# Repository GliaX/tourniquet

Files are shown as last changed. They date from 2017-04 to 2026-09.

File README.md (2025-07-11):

# EXERCISE CAUTION WITH CLINICAL USE Tourniquet


The design of this tourniquet is constantly being improved based on feedback from the field. While we are working very hard to prepare this tourniquet for clinical use, we do not consider it finished. Please do not deploy this unless you are in a crisis situation and know exactly what you are doing. 3D printed tourniquet is to stop bleeding, especially related to penetrating injuries.

Please read our [Design Intent document](https://github.com/GliaX/tourniquet/blob/master/quality_control/design_intent.md) before creating a pull request with any re-designs!

This tourniquet is in use [in Gaza](https://trklou.medium.com/3d-printed-open-source-tourniquet-rationale-failure-analysis-and-proposed-next-steps-of-the-glia-97e8441b4c5a) and is being produced for [emergency use in Ukraine](https://trklou.medium.com/glias-gaza-tourniquet-is-ready-for-emergency-use-in-ukraine-make-some-if-you-can-ef5f83260b7c).

## Contact
Contact person: Tarek Loubani <tarek@tarek.org> or Glia <info@glia.org>
Repository manager: Tarek Loubani

## Print settings
Print the 3MF file, modified to your needs. It's not recommended to edit the meshes - do not facet the windlass, do not squish / scale it for easier printing.

Supports are to be created based on your own printer and support settings. Please reach out if you have any questions.

Approximately 46g of material is needed to print a single copy of the 4 necessary parts.

Material: ABS
* Layer Height: 0.2 mm
* Infill: 100%
* Bed temperature: 100°C temp at the first layer to avoid warping.

Material: PETG
* Layer Height: Same as ABS
* Infill: Same as ABS
* Bed temperature: 85°C temp at the first layer to avoid warping.

### Settings Per Part:
* backing_support:
  * supports
  * 4 perimeter shells/walls
  * 2 bottom/top shells/walls
* buckle:
  * supports
  * 2 perimeter shells/walls
  * 2 bottom/top shells/walls
* clip:
  * supports
  * 4 permiter shells/walls
  * 4 bottom/top shells/walls
* windlass:
  * supports
  * 4 permiter shells/walls
  * 4 bottom/top shells/walls

## Assembly Instructions
See the assembly instruction manuals in the following languages:
* [Arabic](assembly_instructions/INSTRUCTIONS_AR.md)
* [English](assembly_instructions/INSTRUCTIONS_EN.md)
* [Ukrainian](assembly_instructions/INSTRUCTIONS_UA.md)
* [Polish](assembly_instructions/INSTRUCTIONS_PL.md)
* [French](assembly_instructions/INSTRUCTIONS_FR.md)
* [Russian](assembly_instructions/INSTRUCTIONS_RU.md)

## Tourniquet QA (Quality Assurance) Folder
In this QA folder, you will find a printable QA chart and checklist. There is also information on design intent, and tensile strength notes. 
https://github.com/GliaX/tourniquet/tree/master/quality_control

## Tourniquet staging and folding Instructions
There are several reasonable techniques for staging a CAT-style tourniquet. At Glia, we use and recommend the following technique, which is in use in Gaza: https://www.youtube.com/watch?v=CSECJQPJmLw

## Packaging Instructions
The tourniquet should be packaged in clear, thin plastic such as PVC wrap to prevent any degradation from humidity or other environmental factors. This wrap should be easy to remove with bare hands and no tools.

## Injection molding - WARNING
We have presented injection molding files in the [`injection_molding`](injection_molding) folder. The injection molded tourniquet has not yet been deployed and is in the process of being tested at this time. Follow best practices for injection molding and assemble parts as above.
The "desktop_injection" folder is highly experimental and not deployed yet. We give no guarantees to the mold's correct behavior. 

## License
See the [LICENSE file](LICENSE) for more details of the GPLv3 license. These files are also available as [Creative Commons By Attribution ShareAlike](https://creativecommons.org/licenses/by-sa/4.0/) if desired.

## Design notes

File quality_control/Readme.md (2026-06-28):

# Tourniquet Quality Control

Our [Design Intent](design_intent.md) document covers the reason for the specific design of our tourniquet parts. Please read this document before printing the parts.

There are several tools available for Quality Assurance of the manufactured tourniquet.

**Material Specs**

Here are the [Material Specs](Tourniquet_NonPrint_Material_Specs.pdf) for non-printed materials needed. These materials were sourced in Canada, so there will be differences based on your location, but please adhere to the quality of these materials as much as possible, especially with the inner strap. 

**Backplate Tester**

The [Backplate Tester](TQ_backplate_tester.STL) has been developed in order to test the backplates as they come off of the 3D printer bed. This is because of breakage that can be common when printing this part. Please see the [Backplate Breakage Report](Backplate_Breakage_Report.pdf), which talks about this issue, and also shows how to use the backplate tester.

**Strength Test for Parts**

Strength test for Buckle [video](buckle_strength_test.mp4) - insert a strap into both slots and pull apart with hands using maximum strength

Strength test for Backplate [video](backplate_strength_test.mp4)- use backplate tester above to bend backplate around the Diameter

Strength test for Clip [video](clip_strength_test.mp4)- hold both side of the clip and bend them away from each other

Strength test for Rod [video](rod_strength_test.mp4)- push with hands at maximum strength with thumbs on slot and also adjacent to slot

**Strap Spacer**

The [Strap Spacer](strap_spacer.stl) is a tool that can be used in order to ensure the inner strap has the correct slack needed when assembling and sewing the tourniquet together.

The material and printing settings do not matter as long as the dimensions of the spacer are accurate.
This part is a tool, not an integral element of the tourniquet and does not need to meet the rigidity requirements of the windlass, backplate, buckle or clip.

Please see step #10 in the assembly instructions on how to use the strap spacer when manufacturing the tourniquet.

**QA Chart and Checklist**

The Tourniquet [QA Chart](tourniquet_QA_Chart.pdf) and [QC Checklist](tourniquet_QC_checklist_x2.pdf) are tools to be used when conducting a quality assurance check on the finished manufactured tourniquet. These tools ensure that all the details are given attention to check if they adhere to the manufacturing specifications in the assembly instructions, and that the device will function properly when used.

**Measuring Tool**

The [Tourniquet Measuring Tool](tourniquet_measuring_tool.pdf) can be used when conducting the quality assurance of each manufactured device. This is a simple device printed on paper that can help with the QA process in terms of quickly checking that 3 important measurements are correct:

1. the distance from the rounded end of strap to the closest edge of the box stitch (30mm)

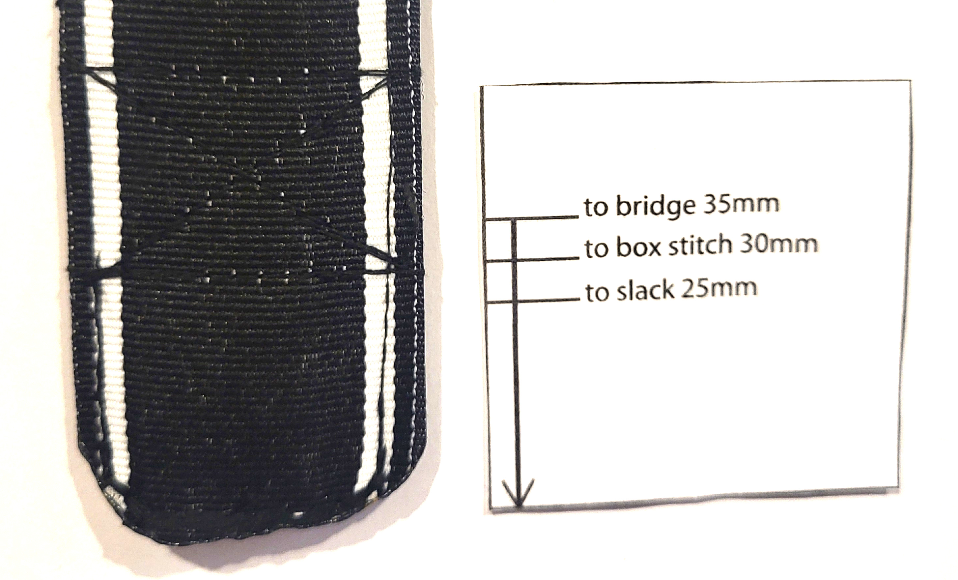
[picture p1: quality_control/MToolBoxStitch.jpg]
Box Stitch

:-

2. the amount of slack on the inner strap (25mm)

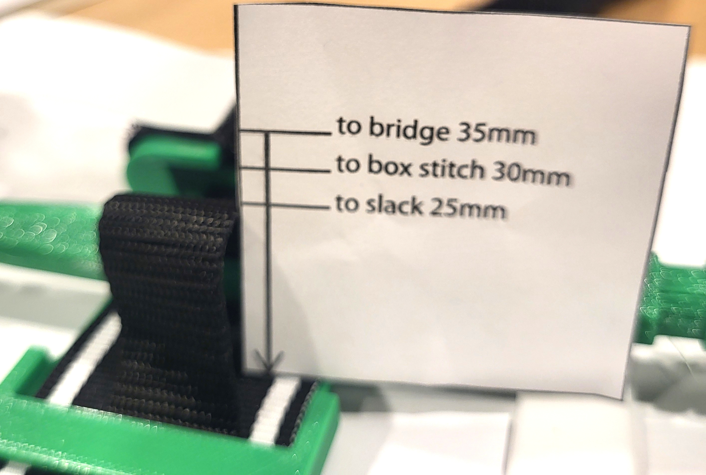
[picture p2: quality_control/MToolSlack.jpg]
Slack

:-

3. the distance from the bridge of the backplate to the stitch holding the buckle to the strap (35mm)

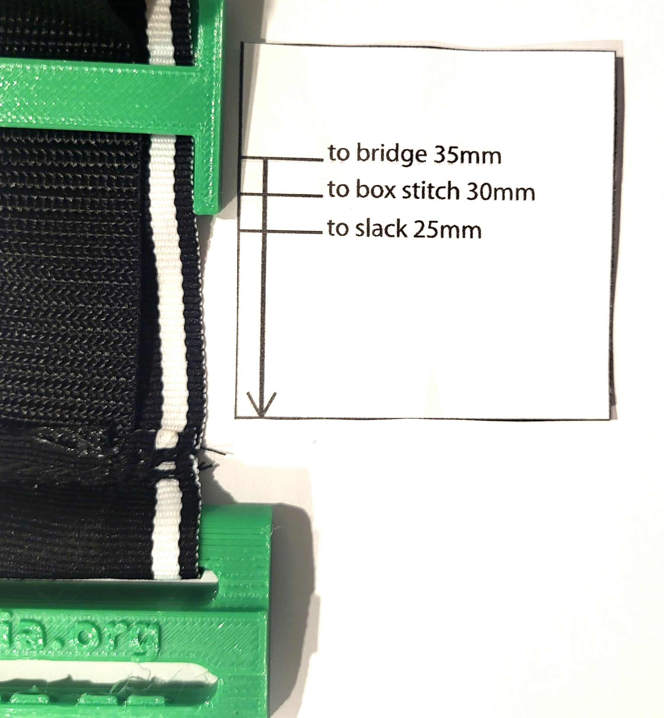
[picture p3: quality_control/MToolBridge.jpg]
Bridge

:-

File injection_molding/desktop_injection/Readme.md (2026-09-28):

# Desktop injection molding 
This folder details the Glia Poland's experimental desktop injection molding process for the plastic parts of the Glia Tourniquet. It details our journey and any pitfalls we have encountered over the months of working at the project, any tips and tricks and the methodology we have established along the way. Please read through it carefully in its entirety before attempting to injection mold your own tourniquet parts. 

# Files
This folder contains files for prototypical molds for all four parts of the Tourniquet to be printed on a resin 3D printer. Each of the molds height is 10cm and they have a universal slot for the aluminium insert that matches our machine's nozzle. The resin compound that is used for printing is brittle and would not withstand the pressure nor the high temperature of the injection molder nozzle so the part of the mold that directly touches it needs to be made of metal, aluminium being the easiest one to machine out. We have provided a file for the insert under the name of "nozzle_slot.FCStd". The nozzle block is split in the middle - when milling you need to put two 2cmx3cmx1cm thick blocks in the vice. 
We also include an edited file for a reinforced windlass and clip used in the molds.  

### Aluminium molds
The folder "aluminium_milled" contains edited molds for milling them out of metal on a 3-axis CNC machine. They will require modification to change over the nozzle shape to the machine that you are using. You should aim to create aluminium molds - the resin is great for prototyping and setting up the machine/testing out plastics, but shatters easily and does not permit long runs. An average aluminium mold longevity is between 2000 - 10000 parts, compared to around 10 using the Siraya Tech Ultra White resin. Stronger engineering resins exist which could provide a longer run, but we have not tested them out.

# Our machine
We are using the [Buster Beagle mk3 injection molding machine](https://www.busterbeagle3d.com/) with the SC100 piston. The mk3 has been confirmed to have enough plastic volume to inject the biggest part of the tourniquet - the windlass. Its main drawback is the weak workholding - a 2 ton vice - which we supplement with [C-clamps](https://www.amazon.com/Edward-Tools-Heavy-Steel-Clamp/dp/B086FRTJF4/). Later on we plan to implement an automated pneumatic vice system that will give us more reliable setting times and ease the handling of the process. 

# Our plastic
Initially we injected the parts with ABS pellet. This proved to be difficult to perform with a DIY injection molder and gave us inconsistent results. The amount of [splay](https://en.wikipedia.org/wiki/Splay_(plastics)) and [delamination](https://en.wikipedia.org/wiki/Delamination) made the parts unacceptable and in effect we decided to switch the plastic to [HDPE](https://en.wikipedia.org/wiki/High-density_polyethylene) which has a better melting and flowing abilities.
We suggest using already coloured, virgin pellets which can be obtained from online retailers or local plastic markets. The pellet needs to be injection molding grade and have an MFI (Melt Flow Index) of minimum 8. Natural white pellets may show discoloration in the part if injected at higher temperatures but is generally easier to inject as color additives often make the HDPE absorb moisture from air and moist plastic needs to be dried before injecting. Powdered pigment can be used in the Buster Beagle machine, although it leads to uneven coloration due to the lack of a mixing screw that is present in larger injection molders.

### What about reground?
Recycled plastic can be used, provided it did not absorb moisture and that the injected part does not perform worse than virgin pellets. Another issue is the fact that recycling companies sometimes mix different plastic subtypes together making it very hard to determine the end result and rigidity of the final part. 

# Anything else I need?
### A compressor
You need a car compressor to power the Buster Beagle piston. We previously used [a small 8 bar 20l compressor](https://sklep.kupczyk.pl/kompresor-tlokowy-fl-24-kupczyk,3,19543,2316), but changed to a larger one after a few months. Currently we are using a [10 bar 115l compressor](https://narzedziapremium.pl/produkt/sprezarka-kompresor-olejowy-115l-v-2065-bjc/) as it's work cycles are longer. It has a regulator at the end, and a quick-release, in case we need to use the compressed air to power something else. A bigger compressor is also needed for the further plans of automating the process. Remember to always wear ear protection when working near a compressor device!

### A small oven
There are [cheap, small ovens](https://www.amazon.com/BLACK-DECKER-TO1313SBD-4-Slice-Toaster/dp/B00GGFHH4U/?th=1) that will be used for drying the pellets and for warming up the molds. They cannot substitute a professional dryer, but cost a fraction of the money and help quite a bit. You should be drying everything hygroscopic that goes into the machine, regardless of the pellets used - whether they are recycled or new. Drying helps immensly with humid environments. Make sure the oven you're buying has a "warm" setting - that it goes under 100 degrees C. 
**Do not use your home oven to dry plastic**

### Alternative to small oven: tumbling dryer
**You probably want a seperate dryer for clothes and for plastic - especially if using colored. This will probably dirty up your clothes with plastic and is possibly a health risk.**
A tumbling clothes dryer works better than an oven on ABS, resulting in strong parts that only have cosmetic defects. You need a cloth sack, fill it with plastic, tie it off with a ziptie and throw it into a dryer. Make sure the heat is set to low - you probably want to be drying the pellets at around 80 degrees C. 

### Alternative to small oven or tumbling dryer: industrial drying machine
To completely solve the moisture problem, you need to have an industrial grade drying machine. They are rather expensive to get, as of 11.05.2023 costing around 2000 euro netto, with other companies reaching 3000 or 4000. There are two technologies that work - either an air powered dryer from a compressor, or one equipped with molecular sieves. You would want a dew point of around -20 degrees Celsius. 

### Safety Eguipment
Always wear a full face mask with a chemical filter while doing injection molding.
Wear overall safety suit and protective shoes and gloves in your workshop, keep them clean and aside from your regular clothes. This is due to the possibility of the fumes and microplastics contaminating your attire.
Always wear ear protecting mufflers when working near an air compressor running. 

**Full Bill of Materials and safety equipment list along with purchase links are available as .ods and .csv files under the name glia_poland_bill_of_materials in the path tourniquet/injection_molding/desktop_injection**

# How do I make a mold?
We are printing our prototype molds in Siraya Tech Ultra White on the Anycubic Photon Mono X 6k. This tutorial assumes you know the basics of resin printing.
We also mill out our molds out of aluminium, which results in molds that we use in production. 
### Safety 
Resin printing is a messy and toxic process, the first steps are to make sure you are safe. Wear nitrile gloves, safety glasses and a respirator or mask. Do not get any of the resin on your skin. Process any trash from the printing by hardening everything using a UV flashlight (wear UV safety glasses when doing this). Do not touch, sniff, throw away uncured parts or supports. Clean any spill with isopropyl alcohol. Have an air purifier with a HEPA filter in your workshop or work in a well ventilated area. [Read safety best practices for resin printing](https://all3dp.com/2/sla-3d-printing-is-3d-printer-resin-toxic/)
### Settings
We are printing with the following settings: 
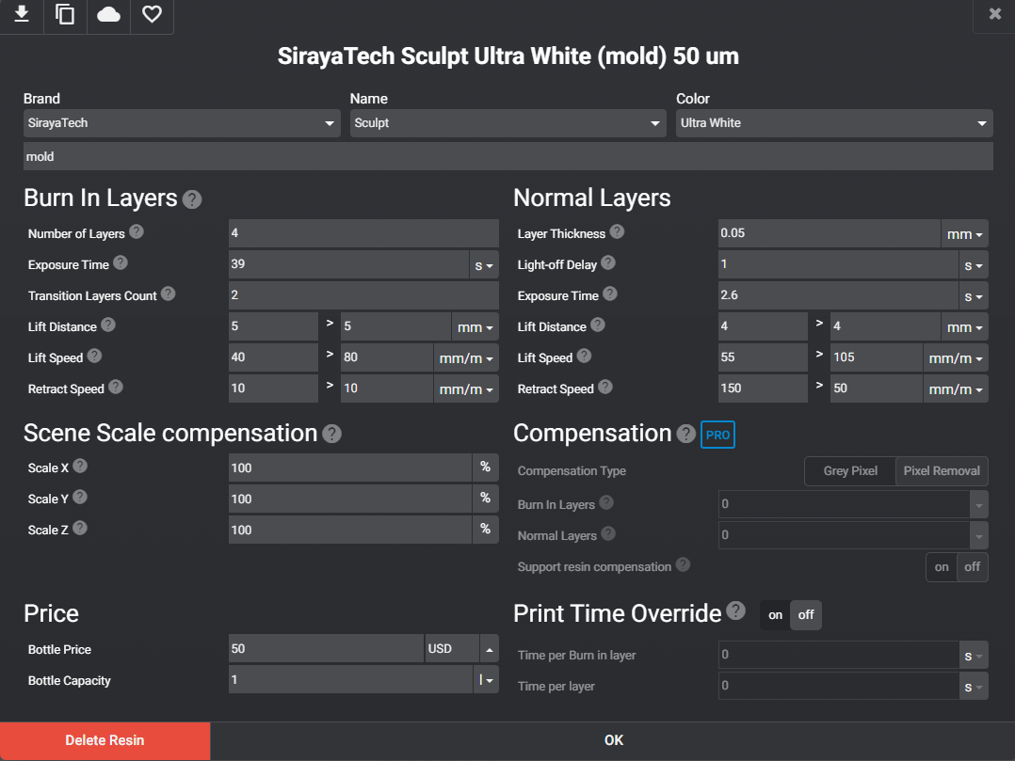
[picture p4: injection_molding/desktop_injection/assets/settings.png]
Illustration 1


### Print orientation
We are printing the molds standing up, off the baseplate, on supports. We have tried other orientations that provide a shorter print, but we encountered issues with the peel forces being too great and ruining it. We angle the print away by 2 - 3 degrees, so the supports don not touch the surface, requiring sanding.  

### Presupporting the file
We use two slicers to prepare files for print. We use PrusaSlicer for its autosupport feature and better supports, then we export the plate with supports and slice the file using Lychee. We need to add more supports on the bottom in PrusaSlicer, see a sample density in the pic below. Otherwise the print falls of the plate under the peel forces/its own weight. We tend to oversupport the print to avoid wasting resin in a failure. 
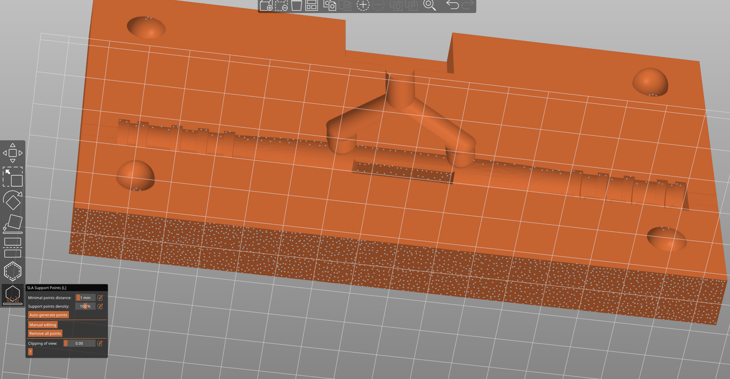
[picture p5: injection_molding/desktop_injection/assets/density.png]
Illustration 2


### Tolerances
Some files might require sanding and fitting. You should be able to open the empty molds without any issue / them getting stuck. 

# Which one do I start with?
The easiest part to inject is the buckle. It has a very small and simple mold that does not require too much resin to print. The cavity survives a lot of injections easily, with the core breaking, so you usually have to reprint just one half of the mold if it shatters. 

# What do I do now? 
**Skipping any of these steps usually ends up with the resin mold shattering and being unusable.**

1. You need an [aluminium nozzle slot machined, example from the BusterBeagle site](https://www.busterbeagle3d.com/product/aluminum-injection-mold-sprue/9?cp=true&sa=true&sbp=false&q=false). It is a small runner section milled/drilled in two alu blocks with the shape of the nozzle for your machine. It should fit the opening at the top of the mold (one half is 2cm x 3cm x 1cm). We have provided a file for the nozzle insert for the Buster Beagle mk3. Do not buy the one from the BusterBeagle shop, that one does not fit the molds. 
2. You need a backing for the molds in the vice. The mold cannot be unsupported, it needs something behind it / in front of it. A piece of MDF works great, or a thick aluminium plate. Make sure it covers the entire mold, and is rigid. 
3. You need [C-clamps](https://www.amazon.com/Edward-Tools-Heavy-Steel-Clamp/dp/B086FRTJF4/) to hold down the mold and prevent it from yawing open. The default vise on the bottom of the machine works up to 2 tons. Add two or three C-clamps on the part that is sticking out of the vise and tighten them down. This prevents  flashing or yawing open the mold. 
4. Make sure the total travel of the nozzle head isn't too big. The nozzle should be around a centimeter from the nozzle block on the mold. Having it go for longer causes your injection to fail, and in extreme situations can break your machine. Don't use the entire travel of the springs to do the injection. 
5. You need a [mold release agent](https://rubberpro.eu/store/pl/srodki-antyadhezyjne-teflonowe/263-maclube-1725-srodek-antyadhezyjny-400ml-spray.html). The plastic tends to grip the molds and doesn't let go despite the draft angles in the design. A mold release spray helps with that. 

**Skipping any of these steps usually ends up with the resin mold shattering and being unusable.**

### Injection machine settings
For HDPE, we are injecting at 240 degrees Celsius, at around 6 bar on the compressor using the SC100 cylinder. These settings may change in the future, and are a starting point, not a requirement. Find something that works for you - that does not break the molds and does not burn your plastic. We have the fastest possible injection speed on the valve for the piston. We heat up our molds in the oven at less than 100 degrees Celsius.

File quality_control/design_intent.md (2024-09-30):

# Design intent

## Plastic selection - do not use PLA
ABS and PETG are acceptable materials to use to print the plastic parts of the tourniquet. PLA is not an acceptable material because it does not withstand exposure to UV light or exposure to the elements well.

## Windlass shape
The windlass must remain cylindrical in shape. This shape does present some inconvenience while printing but this is unavoidable. Support material should be used when printing. Putting a flat face on the windlass will cause the effective diameter of the windlass to not be constant during tightening of the tourniquet. This adds multiple seconds to the time required to apply the tourniquet which is unacceptable.

## Do not change the clip thickness
If the thickness of the clip is changed it will negatively impact the ability of the windlass to secure properly.

## Keep the backing plate and clip separate.
This is important to accommodate small limb sizes. Keeping the parts separate makes them easier to print and allows them to be printed in the orientation best suited to each part.

## Use sections of different lengths of hook and loop instead of one length.
This allows the TQ to dependably catch on itself when applied one-handed as it avoids the scenario where loop meets loop and hook meets hook. However, if using Omnitape then hook and loop exists throughout the entire length of the tape and sectioning is not necessary.

## Adhere to the inner-strap-through-windlass length when assembling.
Changing this length negatively impacts the ability of the windlass to apply effective pressure to against a limb.

## Metal is not necessary for the windlass.
A metal windlass is not necessary and attempting to add metal to a plastic windlass increases complexity without providing any useful benefit. Making the windlass stronger is unnecessary as the windlass is generally one of the last failure points on the tourniquet.

## Nylon SLS printing likely is not viable.
Nylon Selective Laser Sintering (SLS) has not been shown to be an acceptable method of 3D printing for two reasons. First, nylon absorbs water from the atmosphere rapidly over time which will degrade the tourniquet and SLS may negate any tensile strength advantages that nylon has over other approved materials. Second, SLS printers are expensive and not likely to be available in low-resource environments rendering this process impractical. In high-resource environments where such machines are available it is likely more cost effective to pursue injection molding rather than SLS printing.

## Resources

https://trklou.medium.com/3d-printed-open-source-tourniquet-rationale-failure-analysis-and-proposed-next-steps-of-the-glia-97e8441b4c5a

https://trklou.medium.com/3d-printed-tourniquet-day-2-of-gaza-field-trials-ends-badly-may-14-970b3f291e7

https://trklou.medium.com/reinventing-3d-printed-tourniquets-for-ukraine-is-a-mistake-be2937f0ad65

GLIA SLS Initial Evaluation final.pdf in this repository

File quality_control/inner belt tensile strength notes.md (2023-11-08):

# Inner belt tensile strength notes

## Introduction
The tensile strength of the belt in a tourniquet is a concern that is frequently overemphasized. Although the material used for the belt must withstand the forces that will be applied when the tourniquet is used these forces are well within the maximum strength of most commonly available nylon webbing.

## Tensile testing different nylon webbing materials
We tested 4 different samples of 0.75" nylon webbing using a tensile tester. Short lengths of each type of webbing had loops sewn into each end, each sample was loaded into the tensile tester, and force was applied until the sample broke. In every single case the cause of failure was the stitching. More specifically, the stitching tore out of the weave of the nylon strap because the stitching was sewn very close to the edge of the straps used for testing. Two of the samples failed too quickly to gather any useful data, but the remaining two samples withstood over 1100 N (~224 lbf) prior to failure. The results are summarized in the table below.

| Sample | Breaking strength (N) | Mode of failure |
|---|---|---|
|WUXLY|No data|Stitching tear-out|
|MEC|No data|Stitching tear-out|
|Poland|1587|Stitching tear-out|
|ENNS|1167|Stitching tear-out|

## 2nd tensile test
After conducting the first test we sewed a 2nd set of test samples with the stitching set farther from the end than in the first test. Importantly, the thread used to stitch the strapping material together was not the same material that is used in the tourniquets manufactured by Glia and the thread used changed between the first and second tensile tests. This was deemed acceptable because the purpose of this test was to evaluate the strength of the strapping, not to test the stitching.

In every single case what failed was the stitching rather than the strap itself. More specifically, the stitching snapped as its strength was exceeded but the strap itself remained intact. In each case, the failure occurred after being loaded to well over 600 N (135 lb).

| Sample | Breaking strength (N) | Mode of failure |
|---|---|---|
|WUXLY|934|Stitching tear-out|
|MEC|753|Stitching tear-out|
|Poland|1082|Stitching tear-out|
|ENNS|668|Stitching tear-out|

## Webbing specifications
The table below shows contains all of the available information about the strapping used in the test. All values shown are as they are reported from the manufacturer or supplier, they are NOT taken from our test results.

|Parameter|WUXLY|MEC|ENNS|Poland|
|---|---|---|---|---|
|Sample name|WUXLY|MEC|ENNS|Poland|
|Supplier|Wuxly.com|Mec.ca|Enns Textile|pielegnacjaobuwia.pl|
|Part number|UNK*|0407-056|401-1BK-279|Kacperek 250002_IRR|
|Width|2 cm|19 mm|1 in|25 mm|
|Thickness|1.2 mm|UNK|.91 mm|Approx 1.2 mm|
|Composition|70% nylon, 30% Poly|UNK|70% Nylon, 30% Poly|Polyamide|
|Tensile strength|UNK|Approx 453 kg|1265 lb|650 kg|
|Denier|UNK|UNK|840D|UNK|
|Weight|UNK|63 g/m**|16 g/y|UNK|

*Unknown  
**Data obtained from "Q&A" section on website answered by staff. Spec sheet not available.

## Conclusion
Testing the tensile strength of the material used for the belt is extremely important to ensure that it is suitable. However, this concern is often given disproportionate weight compared to more likely modes of failure, such as failure of the stitching securing the webbing. Care should be taken to evaluating the thread used, location of the stitching, and the parameters of the stitches themselves. 

## Attribution
Testing was performed at UWO, [Free Appropriate Sustainability Technology (FAST) Research Group](https://www.appropedia.org/FAST), by Morgan

## Further Reading
For more information on testing the pressure applied by a tourniquet in order to achieve occlusion:
https://www.sciencedirect.com/science/article/pii/S2468067223000494

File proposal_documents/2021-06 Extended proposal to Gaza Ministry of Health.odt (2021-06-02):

Project name

Three stage proposal for providing tourniquets in Gaza

Authors

Dr. Midhat Mhaisen¹, Dr. Bashar Morad², Dr. Mohammed Al-Attar¹, Dr. Dia Abuhasan³, Hany Al-Jafarawy¹, Dr. Tarek Loubani⁴,⁵

Affiliations:

1. Ministry of Health, Palestine
2. Palestinian Red Crescent Society
3. Military Medical Services
4. London Health Sciences Centre
5. University of Western Ontario

Description

Tourniquets save lives and have resulted in a lower than expected mortality rate in Gaza over the past year since the introduction of an active Stop Bleeding campaign and the local manufacture of tourniquets. Unfortunately, tourniquets remain irregularly and poorly stocked in ambulances and emergency departments due to the lack of central funding and a coordinated strategy. Recent attacks by Israeli forces also demonstrate the importance of tourniquet training and distribution to lay citizens in Gaza.

This proposal seeks to address this deficit in a timely and sustainable way. This project divides the Stop Bleeding strategic plan into three components, constituting an incremental staged approach to achieving wide deployment.

Project stages

- Stage 1: Prehospital and hospital provider deployment. Prehospital and hospital providers would receive tourniquets for regular usage and usage during escalations and conflicts.
- Stage 2: High impact community deployment. Tourniquets would be deployed to high impact community sites such as grocery stores, bakeries, convenience stores, places of worship, schools, factories, major offices and athletic facilities. This stage would target 1,000 establishments with 100 tourniquets each.
- Stage 3: Widespread community deployment and training. Wide deployment of tourniquets to citizens' homes as well as all public and private establishments. This stage would also include public education and awareness campaigns to teach citizens about bleeding control.

Objectives

The Ministry of Health will:

- Coordinate and direct national Stop Bleeding strategy in Gaza with prehospital and hospital services
- Ensure sufficient stock for all prehospital and hospital stakeholders
- Acquire tourniquets in Gaza
- Seek international funding in collaboration with World Health Organization
- Coordinate public health campaign for training lay citizens about tourniquets and their usage
- Monitor usage of tourniquets in Gaza

The World Health Organization will:

- Coordinate funding for acquisition of tourniquets in Gaza
- Monitor usage of tourniquets in Gaza
- Seek international funding in collaboration with the Ministry of Health

Prehospital care providers will:

- Ensure each vehicle is stocked with tourniquets
- Provide training to prehospital providers
- Monitor tourniquet usage
- Report any tourniquet device failures in the field

Hospital emergency providers will:

- Ensure appropriate device stocks
- Provide training to hospital providers likely to use tourniquets
- Monitor tourniquet usage
- Report any tourniquet device failures in emergency rooms

Palestinian establishments will:

- Stock “Stop Bleeding” campaign kits
- Ensure kits are easily available and maintained

Palestinian lay citizens will:

- Participate in public education campaigns to learn about tourniquets
- Stock small supplies of “Stop Bleeding” campaign kits for home use

Context

The war in Gaza in 2014 had devastating losses, many of which were related to exsanguination from limb injury. While precise numbers are difficult to obtain due to the nature of the war, it is clear that many deaths were preventable with an appropriate layperson and prehospital awareness of hemorrhage control. If current hemorrhage control practices were in place in 2014, it is expected that several hundred lives would have been saved. While it is still early, emerging data from the 2021 war in Gaza indicate that tourniquet usage may have prevented deaths.

In late 2016, several government and non-governmental agencies started work on a hemorrhage control training program now referred to as the “Stop Bleeding Campaign”. This campaign has trained over two hundred providers and provided thousands of tourniquets for training and deployment in the field.

Unfortunately, there remains no coordinated national strategy for the acquisition and distribution of tourniquets among prehospital and hospital providers across at least four government and non-governmental agencies. As such, there is also no coordinated strategy for funding tourniquets, with all of the tourniquets provided to prehospital providers thus far being donated by Glia Inc and Hayat Centre.

Despite this lack of coordination, it is clear that the current Stop Bleeding Campaign is bearing fruit. Between 30 March 2018 and and 30 March 2019, at least 5,420 out of 6,872 gunshot wounds were to the lower limbs and 549 to the upper limbs, a total of 87.9% of all injuries. Despite this high number, there have been only 12 fatalities from these injuries, representing 0.2% of all limb gunshot wounds.

Many factors are responsible for this unexpectedly low number, including a system-wide emphasis on early trauma care. However, it is certain that the use of tourniquets when available and improvised tourniquets when not available contributed to this disproportionately low mortality rate.

Intended beneficiaries

- Ministry of Health (Palestine) – creation of needed medical devices
- Palestinian Red Crescent Society – continuing training and support of their 3D modeling team
- Military Medical Services
- Civil Defence
- World Health Organization

Strategic partners

- Ministry of Health (Palestine)
- Palestinian Red Crescent Society – continuing training and support of their 3D modeling team
- Military Medical Services
- Civil Defence
- World Health Organization
- International Committee of the Red Cross
- University of Western Ontario (Canada)
- London Health Sciences Centre (Canada)
- Health Canada
- Glia Inc

Methodology and activities

Prediction of future usage during non-emergency

We predicted the usage of tourniquets in prehospital and hospital settings after consultation with providers and leaders in major prehospital and hospital organizations based on current usage patterns.

Note that for several reasons, prehospital usage is expected to be significantly higher than hospital usage, as reflected in the projected usage numbers.

Table 1. Projected prehospital usage of tourniquets

Ambulance service | Total ambulances | Daily active ambulances | Projected annual tourniquet usage
Ministry of Health | 64 | 10 | 400
Palestinian Red Crescent | 60 | 10 | 600
Civil Defense | 13 | 8 | 500
Military Medical Services | 13 | 7 | 400
Total | 150 | 35 | 1900

Table 2. Projected emergency department usage of tourniquets

Hospital | Projected annual tourniquet usage
Al Shifa Hospital | 60
European Gaza Hospital | 60
Indonesian Hospital | 36
Al-Aqsa Hospital | 36
Al-Quds Hospital (NGO) | 36
Al-Awda Hospital (NGO) | 36
Total | 265

Prepositioned stock for use during disaster or crisis

Prepositioned stock should provide tourniquets in the event of a disaster or crisis. Because of the critical and lifesaving nature of tourniquets, we projected a 30-day prepositioned stock to be distributed via the Ministry of Health.

The index casualty rate was derived from the first 30 days of the 2014 war and projected at 7,000 injuries. The limb injury rate was projected from the current Grand March of Return figures at 87.9%, resulting in an expected usage rate of 6,153. Considering stocking and distribution factors, a proposed number of 7,000 tourniquets is suggested for 30-day prepositioned stock.

As tourniquets do not expire, a decreased risk of future hostilities would result in depleting the prepositioned stock to an accepted level over time.

Deployment of tourniquets to high impact community sites

During wars such as those experienced in 2012, 2014 and 2021, it was difficult for prehospital teams to attend to all wounded patients. This was due to the large number of wounded, infrastructure destruction, and direct targeting of prehospital teams. During the 2021 war, targeting of road infrastructure made it difficult to access hospital centers.

A successful international model for Stop Bleeding campaigns such as those in the United States utilizes public establishments as cost effective depots of kits that include tourniquets and other first aid supplies. The second stage of this project would involve deployment of tourniquets and Stop Bleeding kits to high impact community sites such as grocery stores, bakeries, convenience stores, places of worship, schools, factories, major offices and athletic facilities.

This stage would target 1,000 establishments with 100 tourniquets each, distributed according to an assessment of population density and anticipated needs based on previous usage patterns.

Deployment of tourniquets to private homes

The third stage would involve the deployment of tourniquets to private homes for use by lay citizens as part of a public health and education campaign. While a needs assessment would need to be carefully done to assess the exact number, it would be expected to be between 500,000 and 750,000 tourniquets, depending on expected conditions during a conflict.

Tourniquet cost

Depending on the type of tourniquet and the need to import it, tourniquets may cost as little as USD$10 for locally manufactured tourniquets and as much as $40 for imported commercial tourniquets. As there are currently two high quality manufacturers of tourniquets in Gaza, we assumed a USD$10 cost per tourniquet.

Outputs and deliverables

Tourniquet supply across three stages of project

Table 3 shows the expected purchase of tourniquets for normal use and prepositioned stock for prehospital and hospital usage in Stage 1 is listed below. These numbers assume a population growth of 3% and one major conflict every 3 years. Projections are over the next 5 years.

Tables 4 and 5 show expected numbers for Stage 2 and Stage 3 of the project. Table 6 shows the projected combined total if all three stages are implemented simultaneously.

Table 3. Projected tourniquet purchase requirements 2021-2025, Stage 1

Year | Normal use | Prepositioned stock | Total required
2021 | 2 000 | 7 000 | 9 000
2022 | 2 060 | 0 | 2 060
2023 | 2 122 | 0 | 2 122
2024 | 2 186 | 7 000 | 9 186
2025 | 2 251 | 0 | 2 251
Total | 10 619 | 14 000 | 24 619

Table 4. Projected tourniquet purchase requirements 2021-2025, Stage 2

Year | Normal use | Prepositioned stock | Total required
2021 | 500 | 50 000 | 50 500
2022 | 515 | 50 000 | 50 515
2023 | 530 | 0 | 530
2024 | 546 | 0 | 546
2025 | 563 | 5 000 | 5 563
Total | 2 654 | 105 000 | 107 654

Table 5. Projected tourniquet purchase requirements 2021-2025, Stage 3

Year | Normal use | Prepositioned stock | Total required
2021 | 100 | 93 000 | 93 100
2022 | 103 | 100 000 | 100 103
2023 | 106 | 150 000 | 150 106
2024 | 109 | 143 000 | 143 109
2025 | 112 | 145 000 | 145 112
Total | 530 | 631 000 | 631 530

Table 6. Combined projected tourniquet purchase requirements 2021-2025

Year | Total required
2021 | 152 600
2022 | 152 678
2023 | 152 758
2024 | 152 841
2025 | 152 926
Total | 763 803

Quality control and assurance

There are several tourniquets available both locally and through the import market. Because tourniquet failures may result in death or serious disability, quality control and assurance is critical.

A joint task force under the direction of the Ministry of Health and consisting of representatives of prehospital and hospital providers will ensure that tourniquets are of appropriate quality.

International certifications such as CE, FDA or Health Canada can be used to ensure that rigorous quality standards are met.

Training

Training on the use of tourniquets will be covered in a separate complementary proposal.

Public health campaign

A public health campaign will be covered in a separate complementary proposal.

Usage monitoring

A joint task force under the direction of the Ministry of Health and consisting of representatives of prehospital and hospital providers will monitor tourniquet consumption and adjust required annual numbers based on usage patterns in Gaza.

Time frame

One year, renewable. Operating dates are September 1, 2021 to August 31, 2022.

Resources and budget

Tables 7, 8 and 9 show the projected purchases costs based on requirements calculated in Tables 3, 4 and 5. These costs assume a high quality supply ranging from USD$10 for locally-produced tourniquets to USD$40 for imported high quality tourniquets.

The requested budget for 2021-2025 for the implementation of the first year of Stage 1 is $90 000 (USD) based on the realistic low estimate.

Table 7. Projected purchase costs based on high and low cost estimates 2021-2025, Stage 1

Year | Tourniquets | Low estimate (USD$) | High estimate (USD$)
2021 | 9 000 | 90 000 | 360 000
2022 | 2 060 | 20 600 | 82 400
2023 | 2 122 | 21 220 | 84 880
2024 | 9 186 | 91 860 | 367 440
2025 | 2 251 | 22 510 | 90 040
Total | 24 619 | 246 190 | 984 760

Table 8. Projected purchase costs based on high and low cost estimates 2021-2025, Stage 2

Year | Tourniquets | Low estimate (USD$) | High estimate (USD$)
2021 | 50 500 | 505 000 | 2 020 000
2022 | 50 515 | 505 150 | 2 020 600
2023 | 530 | 5 300 | 21 200
2024 | 546 | 5 460 | 21 840
2025 | 5 563 | 55 630 | 222 520
Total | 50 500 | 505 000 | 4 306 160

Table 9. Projected purchase costs based on high and low cost estimates 2021-2025, Stage 3

Year | Tourniquets | Low estimate (USD$) | High estimate (USD$)
2021 | 93 100 | 931 000 | 3 724 000
2022 | 100 103 | 1 001 030 | 4 004 120
2023 | 150 106 | 1 501 060 | 6 004 240
2024 | 143 109 | 1 431 090 | 5 724 360
2025 | 145 112 | 1 451 120 | 5 804 480
Total | 631 530 | 6 315 300 | 25 261 200

Table 10. Combined projected purchase costs based on high and low cost estimates 2021-2025, all stages

Year | Tourniquets | Low estimate (USD$) | High estimate (USD$)
2021 | 152 600 | 1 526 000 | 6 104 000
2022 | 152 678 | 1 526 780 | 6 104 000
2023 | 152 758 | 1 527 580 | 6 104 000
2024 | 152 841 | 1 528 410 | 6 104 000
2025 | 152 926 | 1 529 260 | 6 104 000
Total | 763 803 | 7 638 030 | 30 552 120

Communication strategy

Intra-group communication will be done with in-person meetings coordinated by the Ministry of Health, with email and by telephone between assigned contacts in each stakeholder.

External communication will be via twitter, facebook, instagram and public talks in Gaza and internationally.

Project Proposal Document Tourniquet

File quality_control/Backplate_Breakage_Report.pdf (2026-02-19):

Tourniquet 3D Printed Backplates – Breakage Report

Filament

The Canada lab is printing these backplates in Petg, which is not as robust and flexible as ABS, which is what our Gaza lab prints with. This has been the issue with the tourniquet backplates breaking because Petg can become brittle.

Filament quality is also an issue based on colour, quality and moisture, although difficult to gauge and quantify before printing.

Nozzle Temperature

Nozzle temperature was tested from 215 degrees to 235 degrees, with the same black filament (Duramic). Three backplates were printed with varying nozzle temperatures, and were taken off of the print bed immediately after printing.

Results:
Backplates | 1 st Layer Temp | Printing Temp | Outcome | Photos
#1 | 215 | 225 | Backplate broke at weak points where the thick and thin areas of the part join.

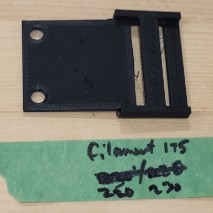
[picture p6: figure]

#2 | 220 | 230 | Backplate did not break at all.

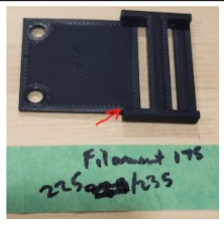
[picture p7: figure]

#3 | 225 | 235 | Backplate slightly cracked at the weak points.

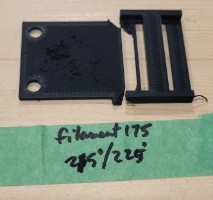
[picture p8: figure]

Bed Temperature

Bed temperature is a major factor in backplate breakage. The default bed temp for Petg is 85 degrees, and this is the appropriate temperature for less breakage. If the ambient temperature is low, 90 degrees is ok. A lower bed temperature than 85 may result in less bed adhesion, and a higher temperature than 85 may result in more breakage due to the temperature difference when the bed cools after printing.

When the backplates are taken off of the hot bed immediately after printing, before the bed cools, there is usually a breakage rate of 0% - 4%.

The cooling bed causes the printed parts to contract, and the thinness of the backplates means that there is more bed adhesion. So, instead of being able to contract, the backplates develop micro-fractures at the weakest points of the part (where the thick and thin areas join), and are more apt to break there. When the backplates are taken off of a cooled bed, the breakage rate is usually 25% - 100%. Although, this can fluctuate based on filament and ambient temperature as well.

Breakage Pattern Photo:

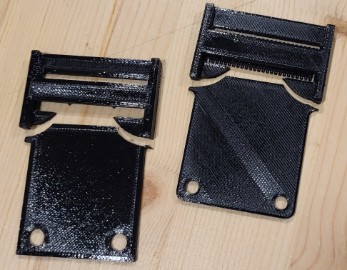
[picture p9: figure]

Ambient Temperature

The difference between the hotbed and the ambient temperature of the space is the biggest factor in the backplate breakage. When there is a bigger difference between the two, and a faster speed from hot to cool, the more breakage occurs.

The difference in temperature from the top shelf of the printer cube in the Glia Canada lab is about 2-4 degrees hotter than the lower shelf. The breakage rate of backplates printed on the top shelf printers is approximately 75-85%, whereas when printed on the lower shelf, the breakage rate is approximately 4-12%. This may also be due to the top shelf having a fan which speeds up the cooling of the hotbed after printing.

The code for the hotbed to cool, M140 S0, was taken out of the gcode files for the backplate, although the hotbed will still cool down automatically 30 minutes after printing, due to safety. However, the prolonged heat on the bed creates a slower cooling rate after 30 minutes and lowers the breakage rate as well.

An ambient temperature of 70-75 F (21-24), and slower cooling of the hotbed, both contribute to lower breakage rates for the backplates.

Conclusion

Use the best filament you can. Black is preferable, as any white pigment added can make it more brittle.

Nozzle temp is best at 230 degrees.

Bed temp is best at 85 degrees.

Ambient temp is best at 75 degrees.

Backplate Tester

The backplate tester on the GliaX tourniquet repo, is a great way to test the backplates when they come off of the printer bed.

https://github.com/GliaX/tourniquet/blob/master/quality_control/TQ_backplate_tester.STL

In order to do a proper test, hold the backplate facing up, and place the thin end into the crevice of the tester. Holding the thin end in the crevice, bend the backplate around the circumference of the tester with even pressure until the free end of the backplate touches the tester. Do not bounce the backplate back and forth. One solid bend is enough to determine the effectiveness of the backplate.

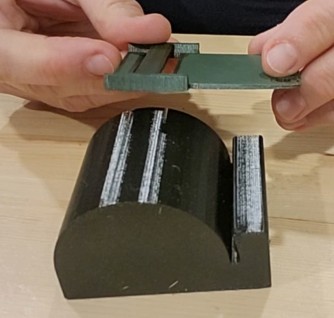
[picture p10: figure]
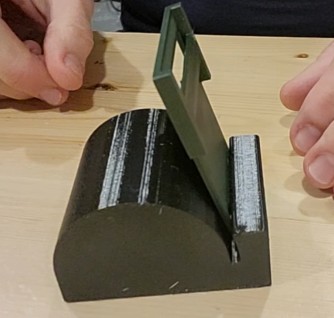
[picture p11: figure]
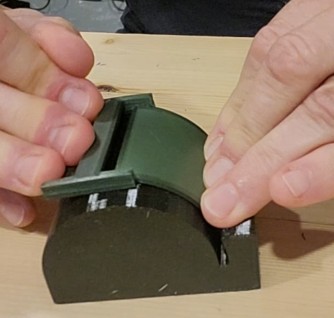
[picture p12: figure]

The tester has a circumference of 5.5 cm, which is the smallest limb it will be able to fit on. If the backplate doesn’t break during the test, it will not break on the tourniquet when used properly.

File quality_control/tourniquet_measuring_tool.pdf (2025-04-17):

to bridge 35mm
to box stitch 30mm
to slack 25mm

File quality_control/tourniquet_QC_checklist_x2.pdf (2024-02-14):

## TOURNIQUET QC CHECKLIST

# Serial Number

# PASS FAIL

### Description of failure:

## ______________________________________________________________ ______________________________________________________________

Tailo

r

Glia

1

Glia

2

Round clean edge sewn closed | ☐ | ☐ | ☐
Box stitch 30mm from round edge | ☐ | ☐ | ☐
No gaps or missing stitches down sides of strap, and between
hook and loop | ☐ | ☐ | ☐
Clip on correctly with caps facing windlass | ☐ | ☐ | ☐
Inner strap moves freely | ☐ | ☐ | ☐
Rivets secure with no wiggle | ☐ | ☐ | ☐
Windlass on correctly between rivets and bridge of backplate | ☐ | ☐ | ☐
Slack on inner strap at windlass is 25mm | ☐ | ☐ | ☐
Distance from bridge of backplate to stich at buckle is 35mm | ☐ | ☐ | ☐
Both inner and outer straps are sewn through the buckle, and
the slot on the buckle that is empty has teeth and faces the end | ☐ | ☐ | ☐

## TOURNIQUET QC CHECKLIST

# Serial Number

# PASS FAIL

### Description of failure:

## ______________________________________________________________ ______________________________________________________________

Tailo

r

Glia

1

Glia

2

Round clean edge sewn closed | ☐ | ☐ | ☐
Box stitch 30mm from round edge | ☐ | ☐ | ☐
No gaps or missing stitches down sides of strap, and between
hook and loop | ☐ | ☐ | ☐
Clip on correctly with caps facing windlass | ☐ | ☐ | ☐
Inner strap moves freely | ☐ | ☐ | ☐
Rivets secure with no wiggle | ☐ | ☐ | ☐
Windlass on correctly between rivets and bridge of backplate | ☐ | ☐ | ☐
Slack on inner strap at windlass is 25mm | ☐ | ☐ | ☐
Distance from bridge of backplate to stich at buckle is 35mm | ☐ | ☐ | ☐
Both inner and outer straps are sewn through the buckle, and
the slot on the buckle that is empty has teeth and faces the end | ☐ | ☐ | ☐

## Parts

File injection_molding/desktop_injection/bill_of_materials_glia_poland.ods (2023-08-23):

 | GLIA POLAND BILL OF MATERIALS
 | Product name | Example brand | Purchase link
WORKSHOP | Injection molder | Buster Beagle Mk3 | https://www.busterbeagle3d.com/product/mk3-parts-bundle/29?cs=true&cst=custom
 | Air compressor | BJC 115L V-2065 | https://allegro.pl/oferta/sprezarka-kompresor-olejowy-115l-v-2065-bjc-13843356330?ev_campaign_id=17958851430
 | Pellet dryer | DEGA AC30 | obtained locally
 | Milling machine | PrintNC | custom made using following instructions: https://wiki.printnc.info/en/home
 | Plastic pellet
 | Aluminium for milling | n/a | obtained locally
SAFETY | Full-face mask with chemical filter | 3M (different sizes) | https://allegro.pl/listing?string=maska%20pe%C5%82notwarzowa%203m
 | Nitrile gloves | Mercator Nitrylex | https://www.matopat24.pl/mercator-nitrylex-classic-rekawiczki-nitrylowe-jednorazowe-100-szt_17622-23715
 | Workshop suit | NeoTools | https://www.mediaexpert.pl/dom-i-ogrod/odziez-robocza/spodnie-robocze/spodnie-robocze-neo-81-240-l-rozmiar-l-52
 | Workshop gloves | n/a | https://allegro.pl/listing?string=r%C4%99kawice%20robocze (https://allegro.pl/listing?string=rękawice%20robocze)
 | Protective shoes | n/a | https://allegro.pl/kategoria/odziez-robocza-i-bhp-buty-robocze-110290
 | Ear mufflers | 3M Peltor Optima | https://allegro.pl/oferta/nauszniki-ochronniki-sluchu-3m-optime-i-10056924514?offerId=10056924514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
TOOLS | Isopropyl Alcohol | n/a | https://allegro.pl/listing?string=alkohol%20izopropylowy
 | Screwdrivers | n/a | obtained locally
 | Pliers (medium sized) | n/a | obtained locally
 | Small cutters | n/a | obtained locally
 | Exacto knife | Olfa AK-4 | https://colorcorner.pl/pl/p/Precyzyjny-noz-OLFA-AK-4/1679
 | Scissors | Olfa SCS-1 | https://allegro.pl/oferta/olfa-nozyczki-scs-1-9938044485?ev_campaign_id=17966335589
 | Riveting station | n/a | https://allegro.pl/oferta/napownica-praska-kaletnicza-nitownica-wyrob-polski-10888072443?ev_campaign_id=19692663265
SEWING | Sewing machine | Juki DDL 8700 | https://szyjposwojemu.pl/pl/p/JUKI-DDL-8700-Stebnowka-jednoiglowa-komplet/2027?shop_campaign=6656148107&gad=1
 | Jeans needles | texi | https://tkaninykaroliny.pl/pl/p/Igly-polplaskie-do-jeansu-grubosc-100-5-szt./2552?gad=1
 | Size 40 Thread | Ariadna TYTAN | https://allegro.pl/oferta/nici-tytan-40-1000m-tapicerskie-kaletnicze-czarne-8699005054?ev_campaign_id=17998709659
 | Omnitape velcro | Halco Omnitape | https://halcoeurope.pl/collections/sew-on-fasteners/products/omni-mixed-hook-loop
 | White Self-Adhesive Hook tape | n/a | https://allegro.pl/oferta/rzep-samoprzylepny-bialy-haczyk-20mm-25mb-12926774244?offerId=12926774244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
 | White Non-Adhesive Loop tape | n/a | https://allegro.pl/oferta/rzep-bialy-20mm-rolka-25m-czesc-miekka-petelka-9543433697?ev_campaign_id=17998709659
 | Polyester Grosgrain Strap 3.8cm wide | n/a | https://allegro.pl/oferta/tasiemka-rypsowa-38mm-czarna-lamowka-kolor-czarny-11104328426?ev_campaign_id=17998709659
 | Nylon Heavy Webbing Strap | n/a | https://pielegnacjaobuwia.pl/pl/p/Tasma-Poliamidowa-25mm-IRR-Wojskowa/6017
 | Double Cap Rivet 7mm head | n/a | https://www.mawrex.pl/nity-kaletnicze/111-nity-kaletnicze-dwustronne-7-mm.html
 | Glue
3D PRINTING | Resin 3D printer | Anycubic Photon Mono X 6K | https://allegro.pl/oferta/drukarka-3d-anycubic-photon-mono-x-6k-23-1litr-12725277820?ev_campaign_id=17958848811
 | Nitrile gloves | Mercator Nitrylex | https://www.matopat24.pl/mercator-nitrylex-classic-rekawiczki-nitrylowe-jednorazowe-100-szt_17622-23715
 | FDM printer | QIDITech X-PLUS | https://outlet3d.eu/pl/fdm/1464-qidi-tech-drukarka-3d-x-plus.html
 | Plastic scraper (for resin printer) | n/a | usually bundled with printer / https://allegro.pl/oferta/szpachelka-lopatka-do-odklejania-wydrukow-3d-9749039147?ev_campaign_id=17966335589
 | Metal scraper (for FDM printer) | Olfa SCR-L | https://colorcorner.pl/pl/p/Skrobak-OLFA-SCR-L/1737
 | UV flashlight | Yato | https://www.mediaexpert.pl/sport-i-rekreacja/turystyka/latarki/latarka-yato-yt-08581
 | UV-proof glasses | NeoTools | https://www.mediaexpert.pl/dom-i-ogrod/odziez-robocza/okulary-ochronne/okulary-ochronne-neo-97-503
 | Resin filters | n/a | https://allegro.pl/oferta/filtr-do-zywicy-3d-10szt-11450277279?ev_campaign_id=17966335589
 | Funnels | IKEA | https://www.ikea.com/pl/pl/p/uppfylld-lejek-jaskrawozolty-80521930/?gclsrc=aw.ds
 | Heat resistant 3D printing resin | Siraya Sculpt Ultra White | https://allegro.pl/oferta/zywica-siraya-sculpt-ultra-white-bialy-1kg-13787520754?ev_campaign_id=17966335589
 | FDM filament | Devil Design | https://allegro.pl/listing?string=devil%20design%20abs
 | Paper towels | n/a | locally obtained
 | Pliers (various sizes) | n/a | locally obtained
 | Exacto knife | Olfa AK-4 | https://colorcorner.pl/pl/p/Precyzyjny-noz-OLFA-AK-4/1679

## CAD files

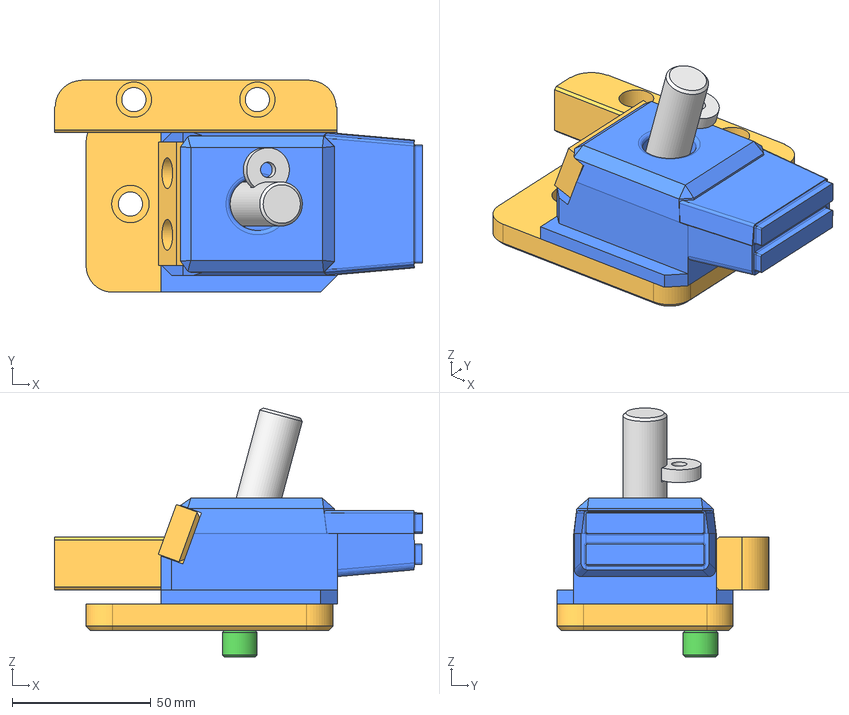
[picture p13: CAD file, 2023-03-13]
injection_molding/Glia Tourniquet Inj-Mold Design (FreeCAD)/sliderAssy.FCStd
132.4 x 76.5 x 89.6 mm
wearPlateA
wearPlateB
squaregib x 2
slide
horn pin
keeper puck
slide retainer

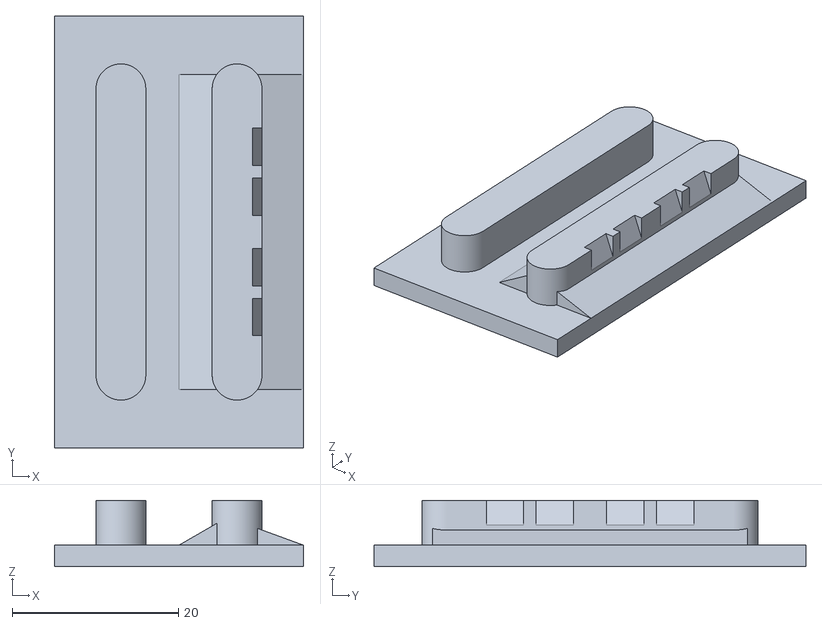
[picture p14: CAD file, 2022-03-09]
injection_molding/buckle_back.stl
30.0 x 52.0 x 8.00

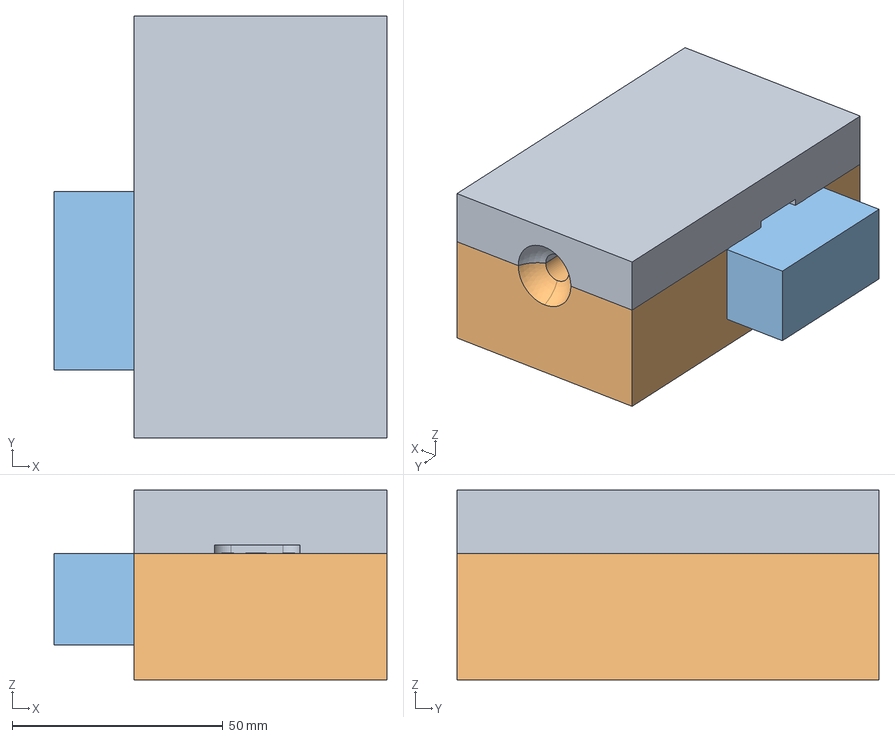
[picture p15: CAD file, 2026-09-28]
injection_molding/desktop_injection/aluminium_milled/clip_injection_mold_milling.FCStd
79.0 x 100.0 x 45.0 mm
clip_core
clip_cavity
clip_insert

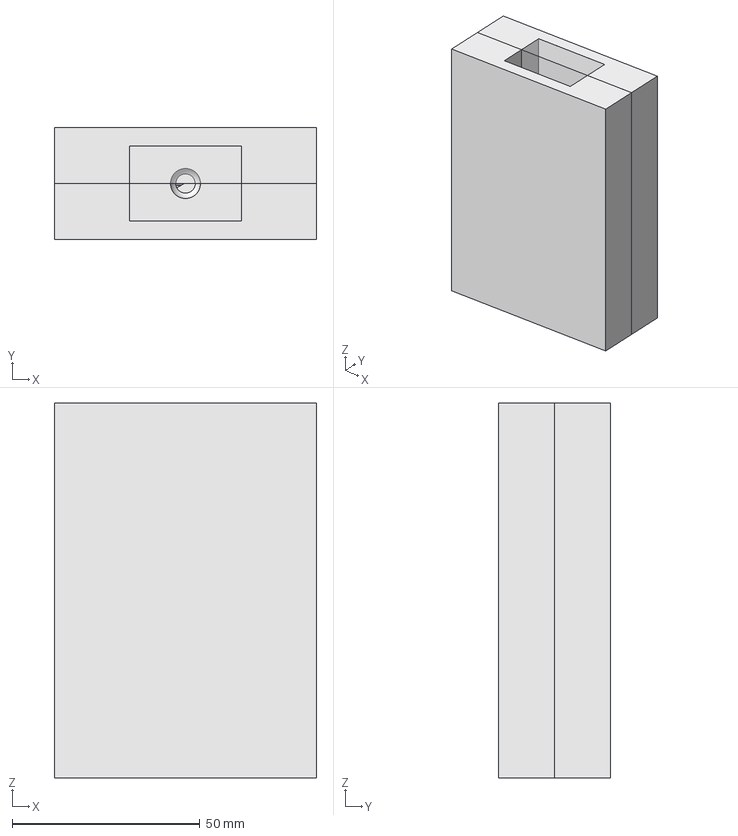
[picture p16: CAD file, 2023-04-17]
injection_molding/desktop_injection/buckle_injection_mold_tolerances.FCStd
70.0 x 30.0 x 100.0 mm
blank
Mold_B
Mold_A

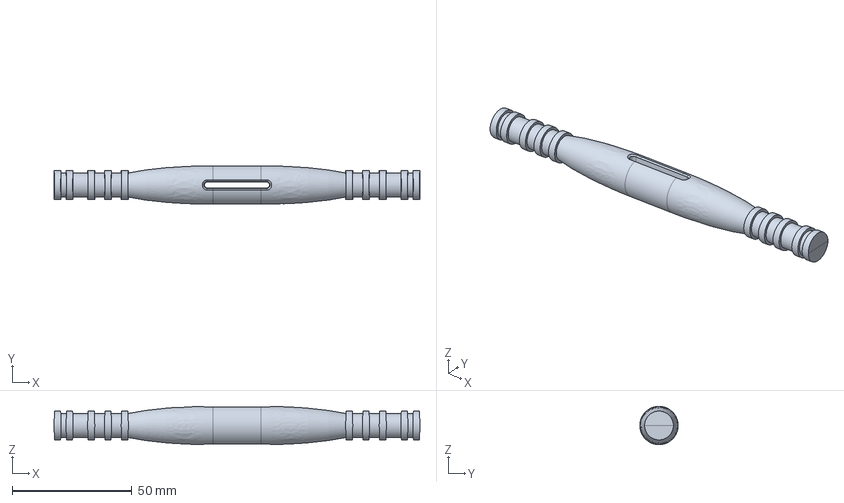
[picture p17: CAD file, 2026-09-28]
injection_molding/desktop_injection/edited models/windlass.FCStd
152.5 x 16.0 x 15.9 mm

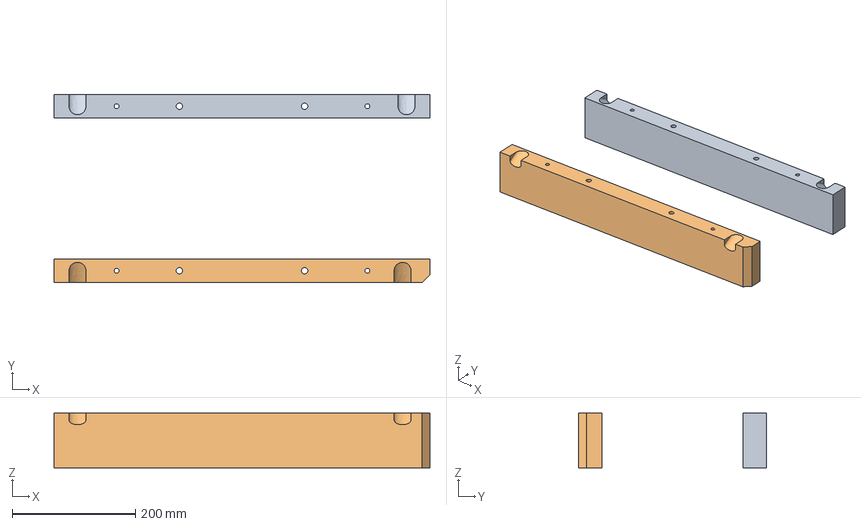
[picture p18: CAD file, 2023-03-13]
injection_molding/Glia Tourniquet Inj-Mold Design (FreeCAD)/rails.FCStd
609.6 x 304.8 x 88.9 mm
rail a
rail b

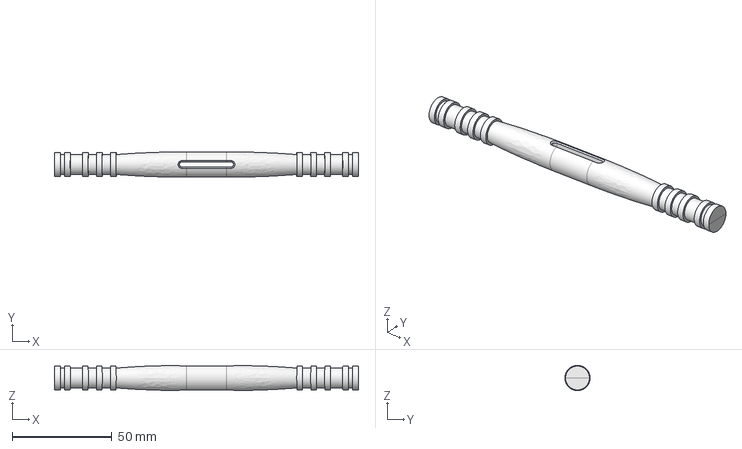
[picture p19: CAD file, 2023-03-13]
injection_molding/Inj. Molding Part Models (FreeCAD)/windlass.FCStd
152.5 x 12.7 x 12.7 mm

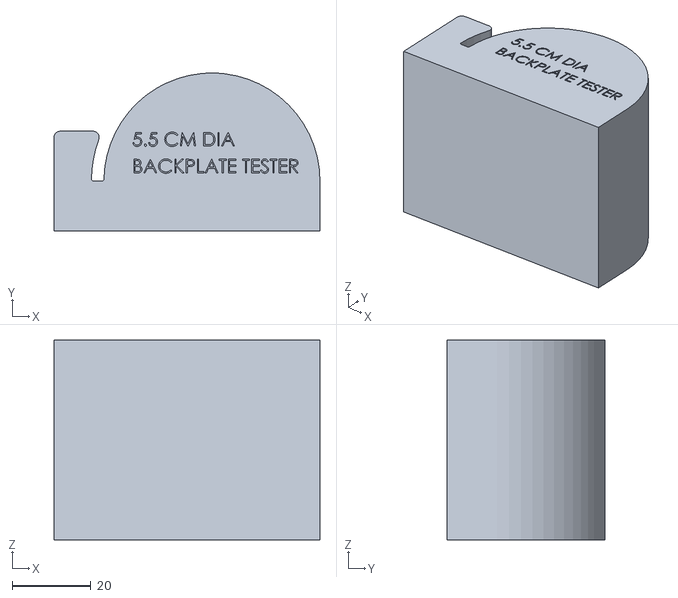
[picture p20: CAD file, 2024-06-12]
quality_control/TQ_backplate_tester.STL
67.7 x 40.2 x 50.8

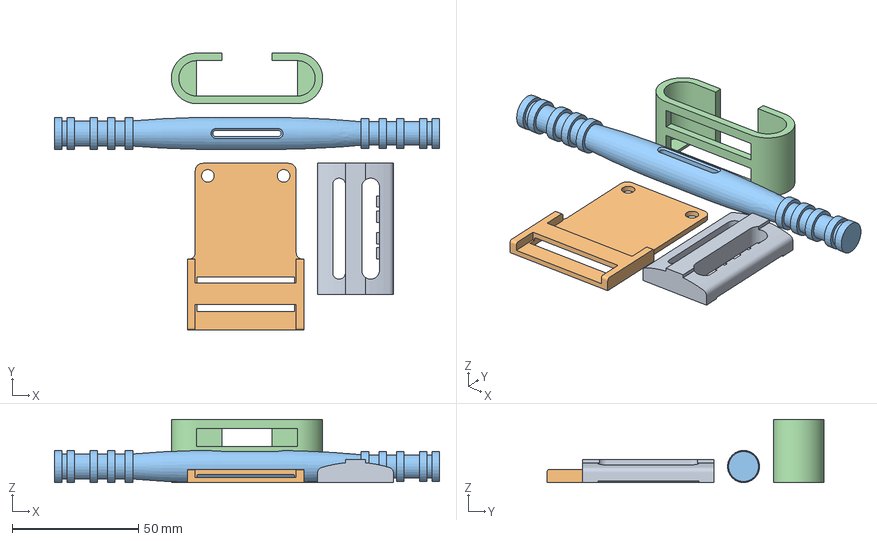
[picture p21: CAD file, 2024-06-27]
tourniquet.3mf
152.5 x 109.6 x 25.0 mm
buckle V2 without logo.stl
backing plate V2.stl
windlass V2.stl
clip V2.stl

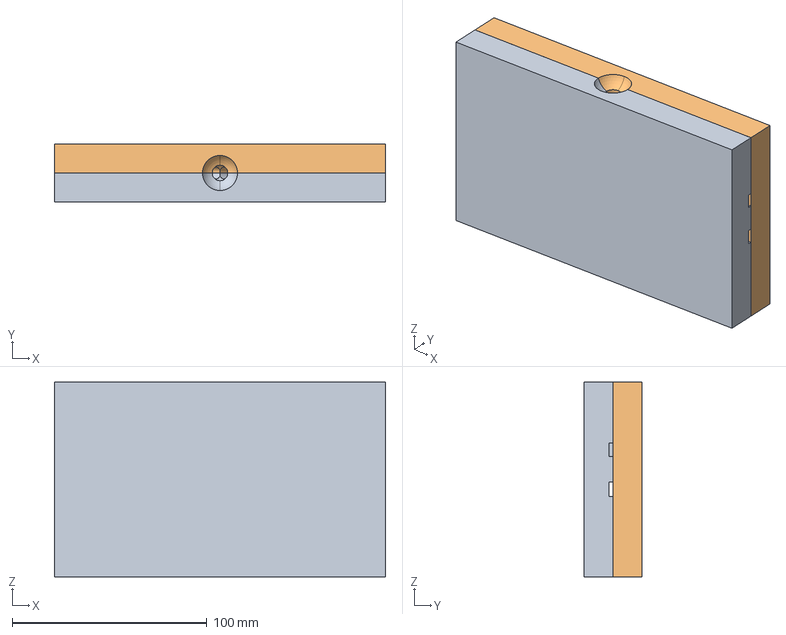
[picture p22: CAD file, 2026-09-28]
injection_molding/desktop_injection/aluminium_milled/windlass_injection_mold_milling.FCStd
170.0 x 30.0 x 100.0 mm
Windlass_Mold_A
Windlass_Mold_B

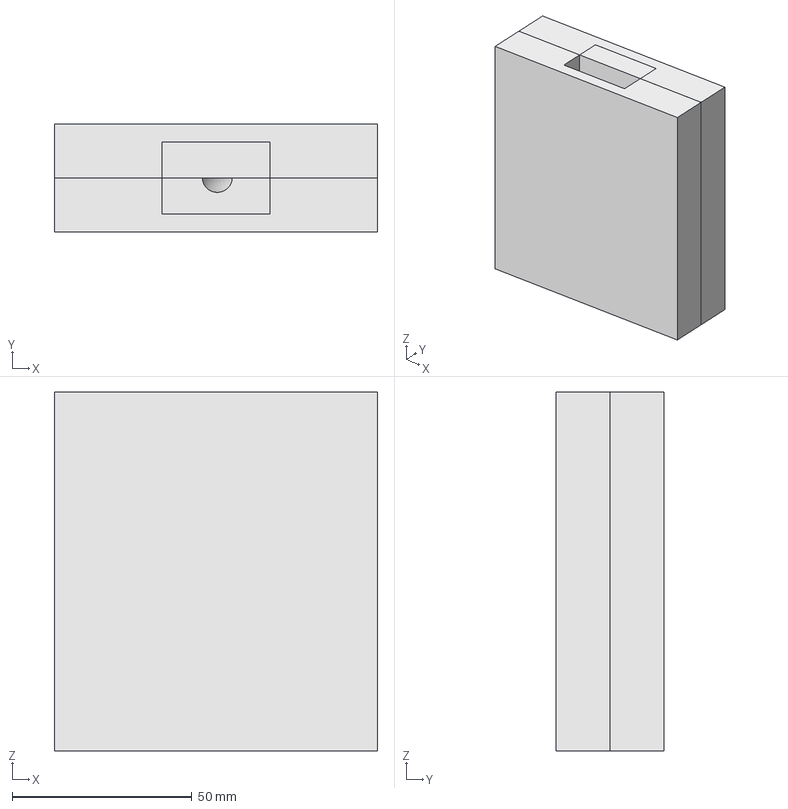
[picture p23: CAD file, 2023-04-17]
injection_molding/desktop_injection/backing_plate_injection_mold_tolerances.FCStd
90.0 x 30.0 x 100.0 mm
blank
jays86A00191v1mh005
Mold_A
Mold_B

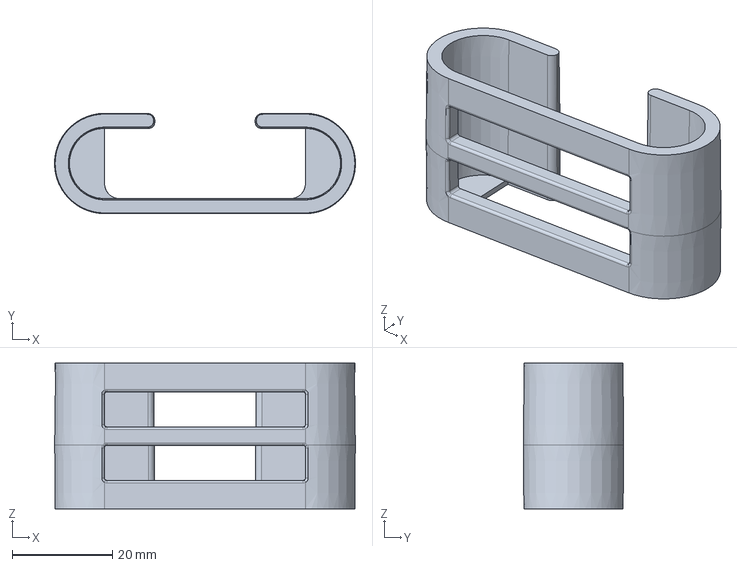
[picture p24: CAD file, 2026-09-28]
injection_molding/desktop_injection/edited models/clip.FCStd
60.0 x 20.0 x 29.0 mm

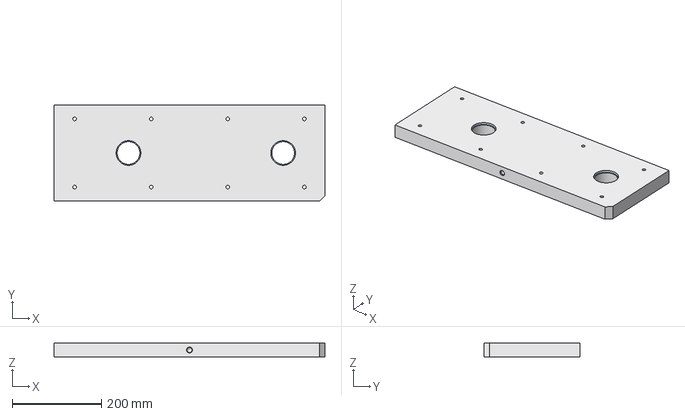
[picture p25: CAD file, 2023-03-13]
injection_molding/Glia Tourniquet Inj-Mold Design (FreeCAD)/ejector plate.FCStd
606.4 x 215.9 x 31.8 mm

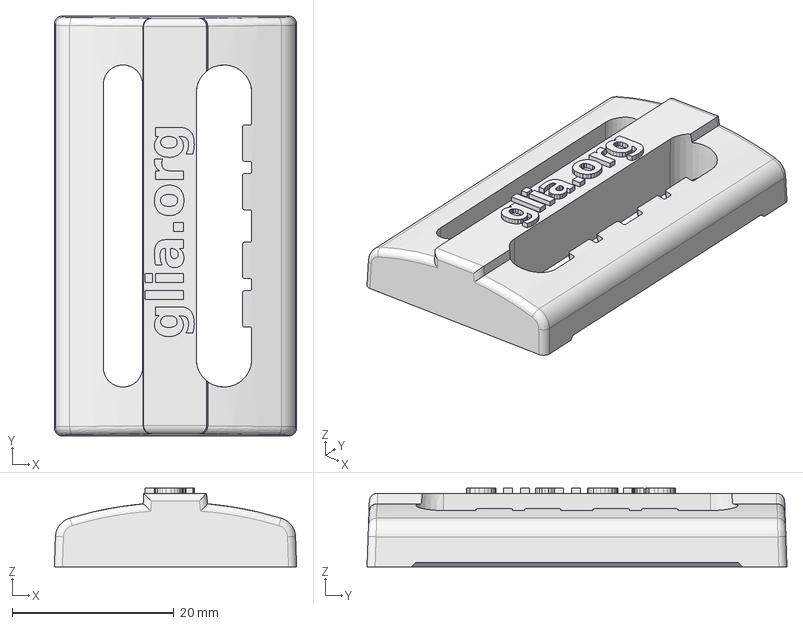
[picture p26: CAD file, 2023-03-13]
injection_molding/Inj. Molding Part Models (FreeCAD)/buckle.FCStd
30.0 x 52.0 x 9.75 mm

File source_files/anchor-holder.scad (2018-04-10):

holder_h=20;        //anchor holder hight
holder_w=60;        //anchor holder
holder_t=25;        //anchor holder wthikness
holder_wall_t=3;    //anchor holder wall thickness
holder_support_t=1;
top_window_w=20;


strap_w=40;          //wide strap width
    //anchor holder width = wide strap width+20
strap_t_cut=7;      //cut width for the strap
//Calcs
h_displace=(holder_t-(2*strap_t_cut))/3;

difference(){//shaping the holder
hull(){//outer body of the holder
cylinder(r=holder_h/2,h=holder_t);
translate([holder_w-holder_h,0,0])cylinder(r=holder_h/2,h=holder_t);
}
//internal cut
translate([0,0,holder_support_t])hull(){
cylinder(r=holder_h/2-holder_wall_t,h=holder_t);
translate([holder_w-holder_h,0,0])cylinder(r=holder_h/2-holder_wall_t,h=holder_t);
}

//rear opening
translate([0,holder_wall_t-holder_h/2,0])cube([holder_w-holder_h,holder_h-(2*holder_wall_t),holder_support_t]);

//top window
translate([(holder_w-holder_h-top_window_w)/2,0,0])cube([top_window_w,holder_h,holder_t]);

//strap_cuts
translate([0,-holder_h/2,h_displace])cube([strap_w,holder_wall_t+.2,strap_t_cut]);

translate([0,-holder_h/2,strap_t_cut+h_displace*2])cube([strap_w,holder_wall_t+.2,strap_t_cut]);

}

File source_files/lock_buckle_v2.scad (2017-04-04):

/*lock buckle is the same as the lock buckle you will find in bags laces
this element could be used in the tourniquet to tighten the strap for the first time before the final tightening by the windlass
will allow you pull the strap but will not go back whwn you let it

*/
rad=2;//cylinders radiuses
strap_w=25;//width of the strap in mm
wall_t=3;//thickness of the side walls in mm
$fn=50;
length=20;//buckle length
angle=-45;//positioning the cylinders
rear=4;//rear end bar thickness

/////////////////////////////////////
///////////////////////////////////////

rotate([0,angle,0])translate([length/2+wall_t,0,-rad])rotate([-90,0,0])cylinder(r=rad,h=strap_w+2*wall_t);//first cylinder to roll the strap"active"
translate([length,0,2*rad])rotate([-90,0,0])cylinder(r=rad,h=strap_w+2*wall_t);//second cylinder it sew the other end of the strap

    translate([1.5*length,0,0])cube([rear,strap_w+2*wall_t,rear]);//rear end of the bckle to hold the static strap end
difference(){//building the side walls
hull(){//objects hulled together to make the shape of the wall
rotate([0,angle,0])translate([length/2+wall_t,0,-rad])rotate([-90,0,0])cylinder(r=2*rad,h=wall_t);

translate([length,0,2*rad])rotate([-90,0,0])cylinder(r=2*rad,h=wall_t);

translate([-1,0,0])cube(wall_t);
    translate([1.5*length,0,0])cube([rear,wall_t,rear]);
}
translate([length/1.5,0,-length/1.5+wall_t])rotate([-90,0,0])cylinder(r=length/1.5,h=wall_t+.1);
//the curcular cun in the bottom of the walls
}


translate([0,strap_w+2*wall_t,0])//building the other wall "same but mirrored
mirror([0,1,0])
difference(){
hull(){
rotate([0,angle,0])translate([length/2+wall_t,0,-rad])rotate([-90,0,0])cylinder(r=2*rad,h=wall_t);

translate([length,0,2*rad])rotate([-90,0,0])cylinder(r=2*rad,h=wall_t);



translate([-1,0,0])cube(wall_t);
    translate([1.5*length,0,0])cube([rear,wall_t,rear]);
}
translate([length/1.5,0,-length/1.5+wall_t])rotate([-90,0,0])cylinder(r=length/1.5,h=wall_t+.1);
}

//bar
difference(){//the front end of the buckle with angled cut to go with the strap
translate([-1,0,0])cube([wall_t+1,strap_w+2*wall_t,wall_t]);
    rotate([0,angle,0])translate([0,0,-wall_t])cube([2*wall_t,strap_w+2*wall_t,wall_t]);
}

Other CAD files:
injection_molding/Glia Tourniquet Inj-Mold Design (FreeCAD)/Assembly.FCStd
source_files/CAD/windlass.FCStd
injection_molding/windlass.stl
lock_buckle_v2.stl
injection_molding/Glia Tourniquet Inj-Mold Design (FreeCAD)/core clamp plate.FCStd
injection_molding/Glia Tourniquet Inj-Mold Design (FreeCAD)/guidePin.FCStd
injection_molding/Glia Tourniquet Inj-Mold Design (FreeCAD)/parameter-container.FCStd
injection_molding/Glia Tourniquet Inj-Mold Design (FreeCAD)/retainer plate.FCStd
injection_molding/Glia Tourniquet Inj-Mold Design (FreeCAD)/shot.FCStd
injection_molding/Inj. Molding Part Models (FreeCAD)/backing_support.FCStd
injection_molding/Inj. Molding Part Models (FreeCAD)/clip.FCStd
injection_molding/backing_support.stl
injection_molding/buckle_front.stl
injection_molding/clip_moving_part.stl
injection_molding/clip_stationary_part.stl
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

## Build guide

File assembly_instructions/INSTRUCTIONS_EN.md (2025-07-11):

# Bill of materials

|Black Non-Adhesive<br>Hook and Loop Tape<br>3.8cm wide (1.5”)<br>for front face<br>of external belt|White Self-Adhesive<br>Hook and Non-<br>Adhesive Loop Tape<br>1.9cm wide (.75”)<br>for clip|Polyester Grosgrain<br>Strap<br>3.8cm wide (1.5”),<br>0.5mm thick<br>for back face<br>external belt|Nylon Heavy Webbing<br>Strap **no stretch at all**<br>1.9cm wide (.75”),<br>1mm thick<br>for internal belt|
|:-------------------------|:-------------------------|:-------------------------|:-------------------------|
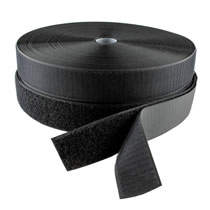
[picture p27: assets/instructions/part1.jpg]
Black self-adhesive hook and loop tape
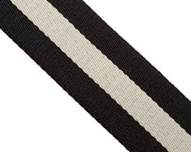
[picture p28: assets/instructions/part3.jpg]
Polyester grosgrain strap
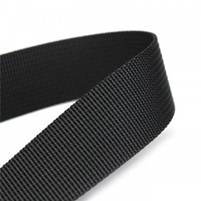
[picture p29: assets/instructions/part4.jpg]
Nylon heavy webbing strap
||White self-adhesive hook and loop tape|||

|Double Cap Rivet<br>7mm head|Strong Polyester Thread<br>We use Tex-40 TK50/2<br>Poly Poly Core|Cyanoacrylate (Super Glue)<br>for ABS, or<br>90 second Epoxy Adhesive <br>for PETG|
|:-------------------------|:-------------------------|:-------------------------|
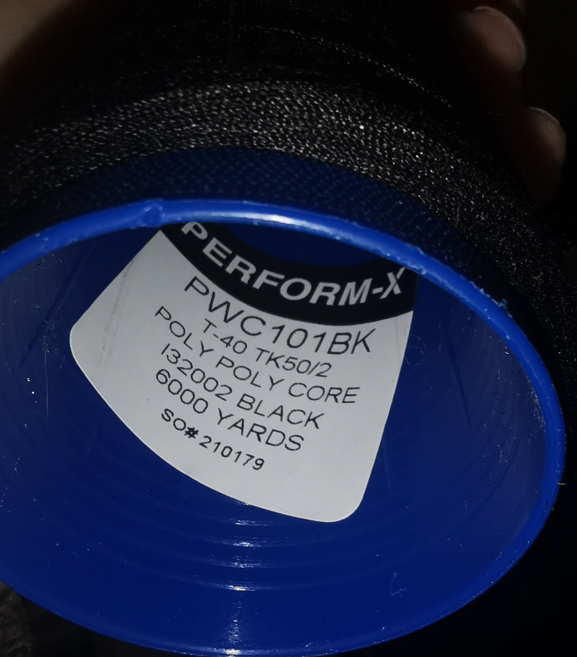
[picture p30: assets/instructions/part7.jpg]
thread
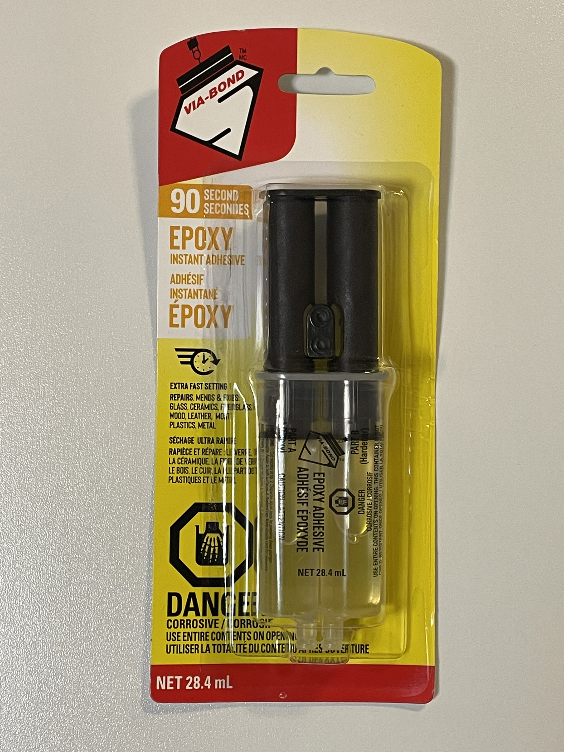
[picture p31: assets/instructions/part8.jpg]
glue
|Double cap rivet|||

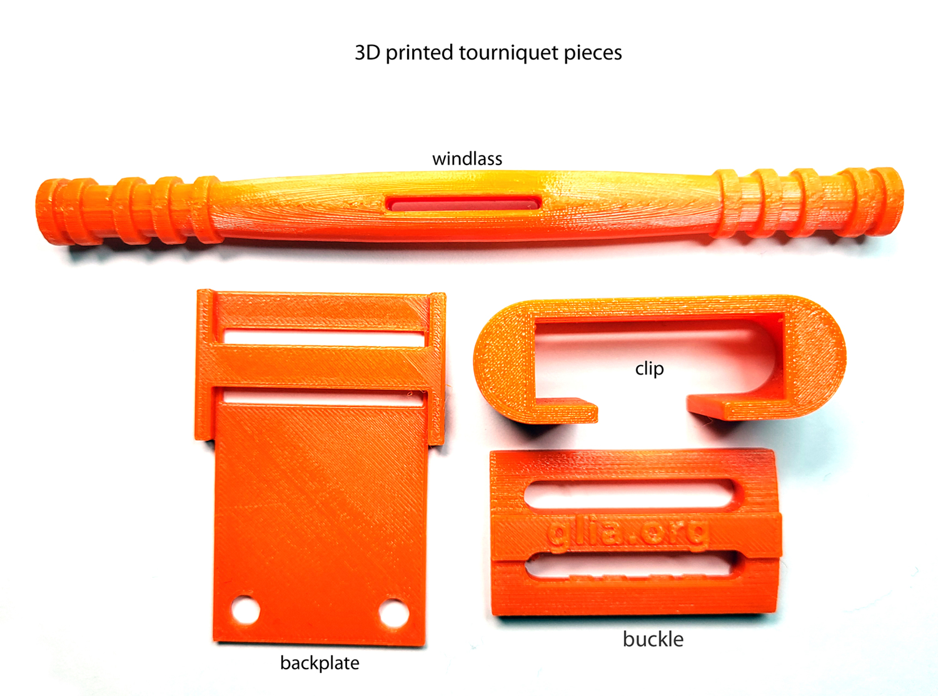
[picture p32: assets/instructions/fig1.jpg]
||
|:-------------------------|
<br>Instructions and details for printing plastic parts for this tourniquet is on Glia’s GitHub site at:
https://github.com/GliaX/tourniquet

# Assembly Instructions
1. Cut all the strapping, hook and loop to the required lengths specified in the table below:

|Material|Quantity|Length|
|:--------------------------------------|:-------------------------|:-------------------------|
|Black Non-Adhesive Hook 4 cm wide|3|6cm|
|Black Non-Adhesive Hook 4 cm wide|1|15cm|
|Black Non-Adhesive Loop 4 cm wide|1|6cm|
|Black Non-Adhesive Loop 4 cm wide|2|12.5cm|
|Black Non-Adhesive Loop 4 cm wide|1|19cm|
|Polyester Grosgrain Strap 4 cm wide|1|92cm|
|Nylon Heavy Webbing Strap 2 cm wide|1|95cm|
|Adhesive Hook 2 cm wide|1|16cm|
|White Non-Adhesive Loop 2 cm wide|1|17cm|
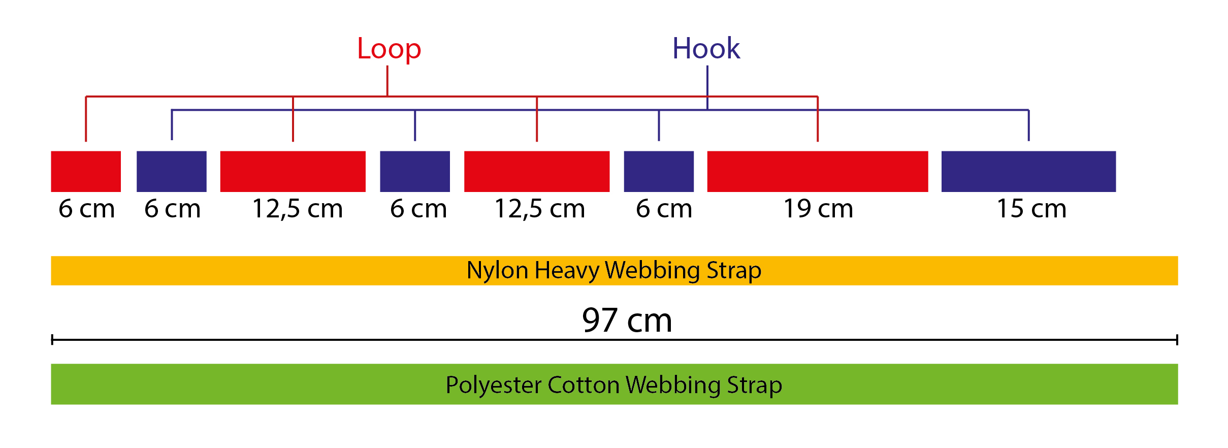
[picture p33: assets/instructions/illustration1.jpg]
Illustration 1

<p>
<p>
*Please keep in mind, the Polyester Cotton Webbing Strap in the above graphic, is actually the Polyester Grosgrain Ribbon in the table above the graphic. It's referenced at the lengths in the table due to the Canada office wanting zero waste of the strapping, or as little as possible. The graphic has both inner and outer strapping at 97cm, which works, but may have some excess strap to trim. it's probably safer to start with 97cm for initial device.*
<p>
<p>
2. For the front face of the belt, begin by placing the Hook and Loop in order of how they will be sewn together. The first piece to sew is the 6cm Loop to the 6cm Hook at the rounded end of the belt.

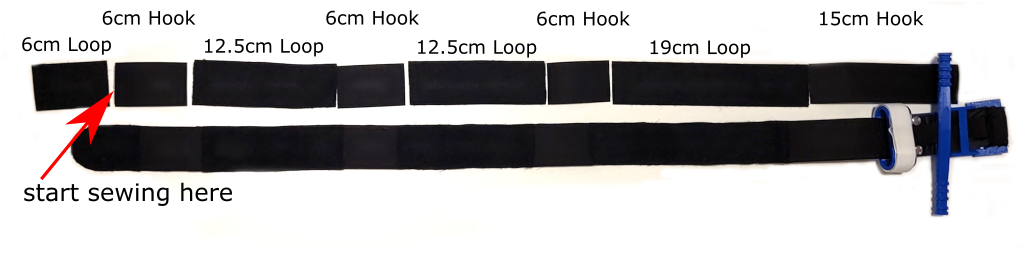
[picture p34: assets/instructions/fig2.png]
||
|:-------------------------|

3. Sew pieces together sequentially in a cascading pattern by placing the edge of each piece above the edge of the next piece and then sewing across them along the seam a couple of times with a zigzag stitch. This type of assembly increases tensile strength, and facilitates a smooth pull through the buckle.

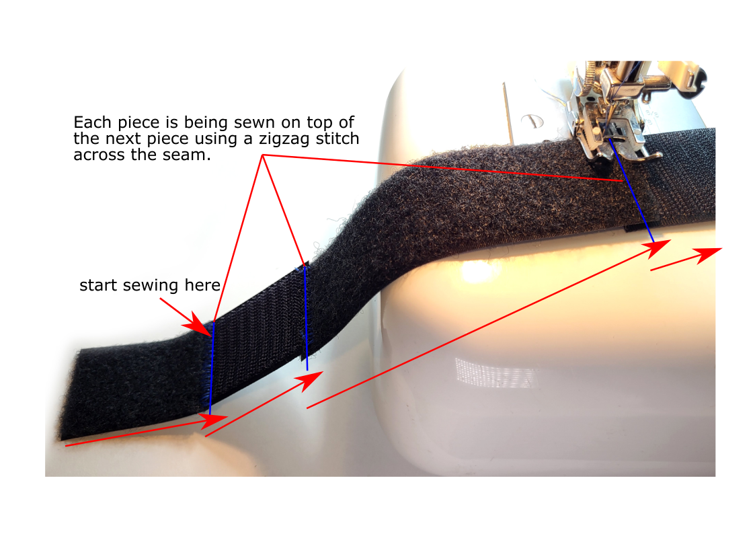
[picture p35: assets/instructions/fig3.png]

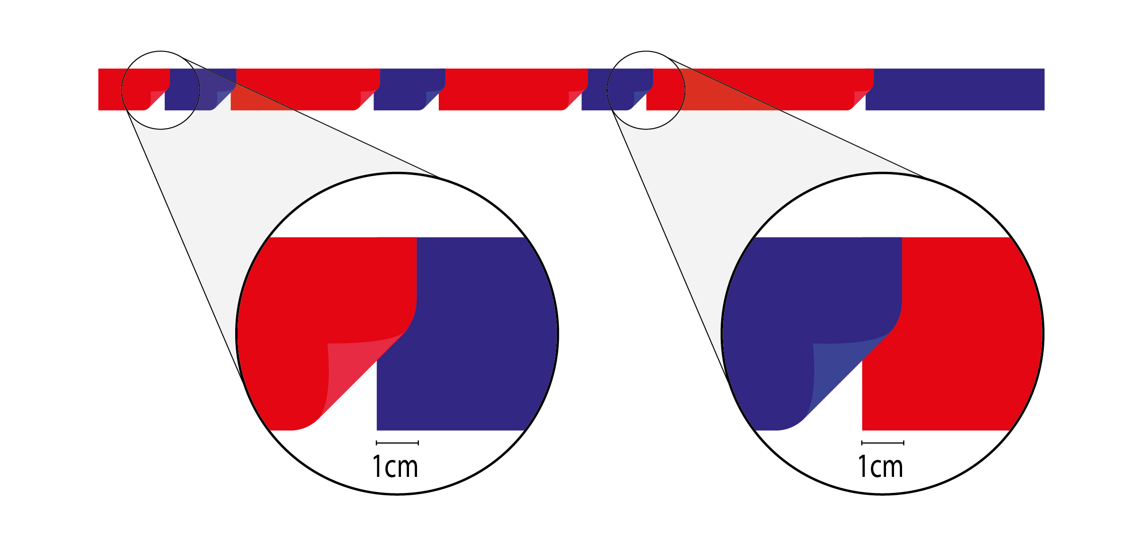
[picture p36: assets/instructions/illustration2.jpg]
Illustration 2

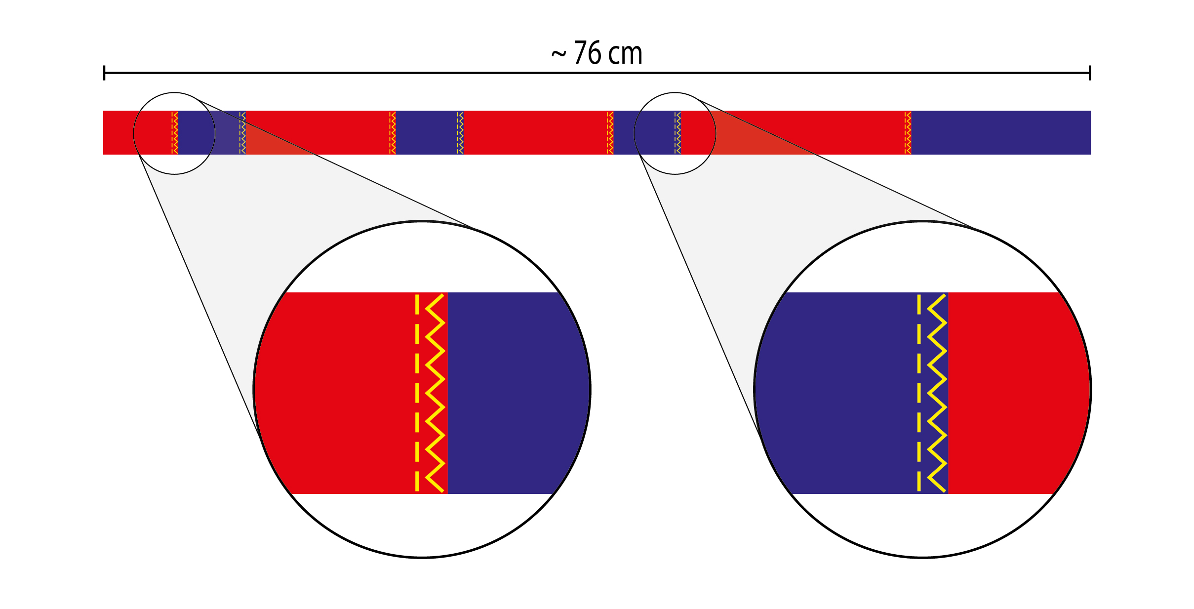
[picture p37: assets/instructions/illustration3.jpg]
Illustration 3


4. Sew the polyester grosgrain strap (3.8cm wide) to the Hook and Loop assembly just sewn, making sure that the Hook and Loop is facing outward. Sew one long side only and leave the other side free to insert the internal belt. (For alternative method of inserting internal belt, please see Addendum at the bottom of these Tourniquet Assembly Instructions.)

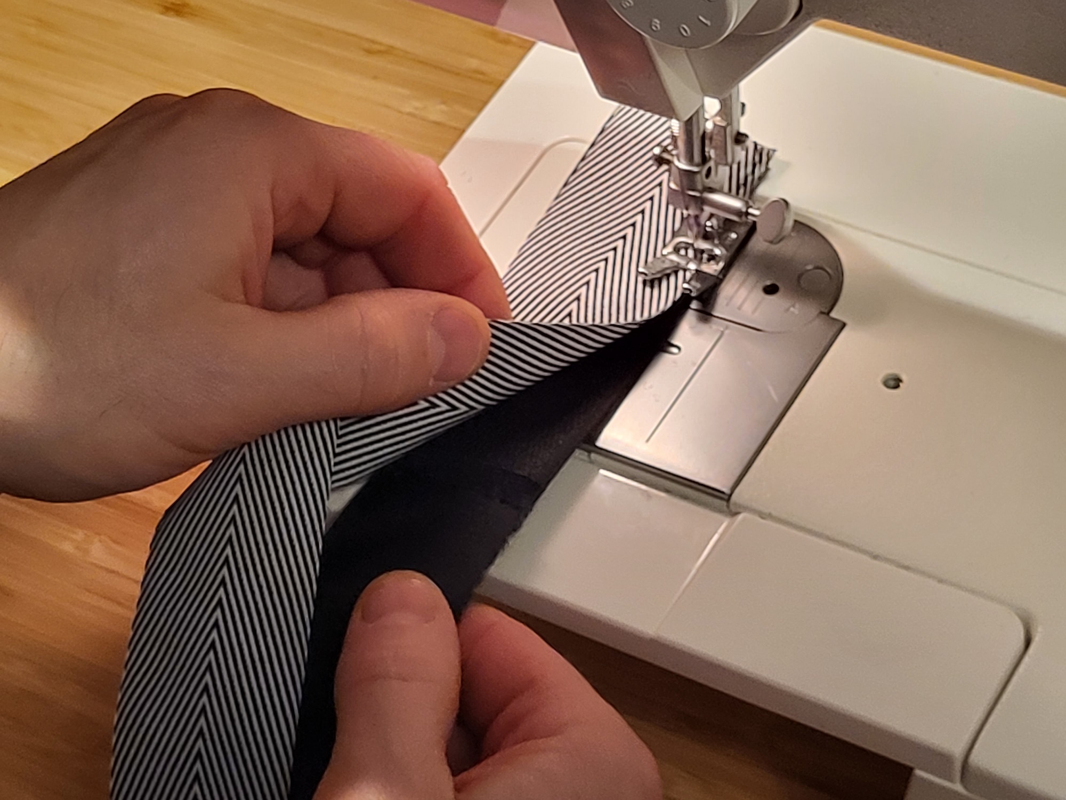
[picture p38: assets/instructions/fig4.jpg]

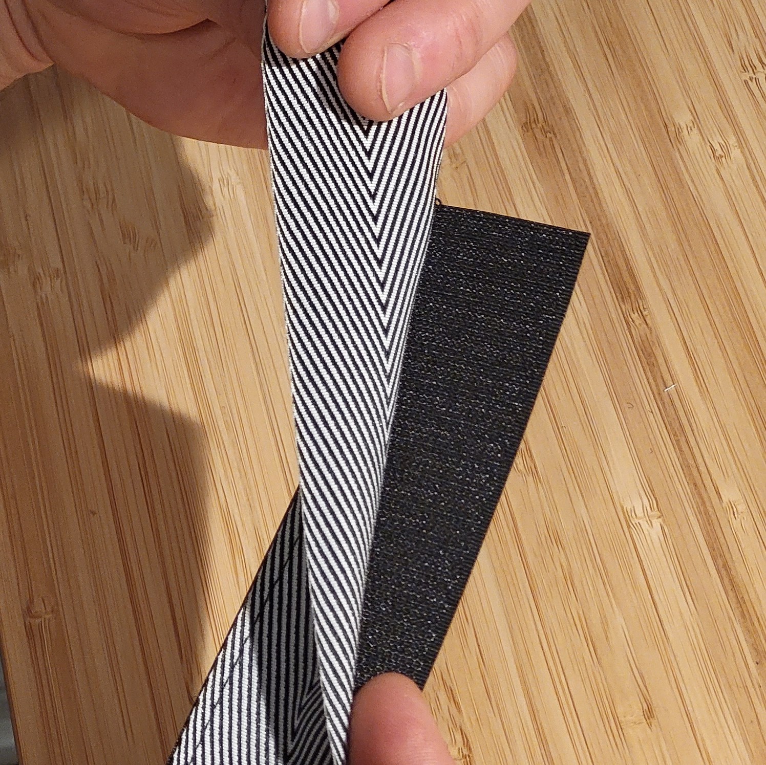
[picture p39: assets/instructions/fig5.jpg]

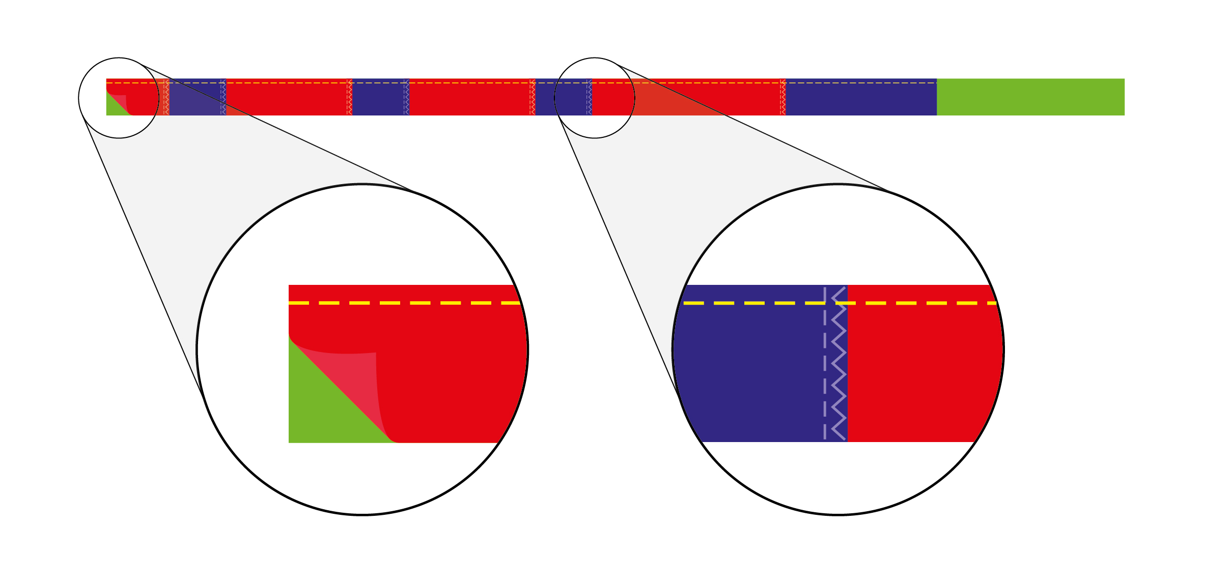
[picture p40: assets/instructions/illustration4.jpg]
Illustration 4


5. Insert the internal belt between the front and back of the external belt, and then sew across the internal and external belts with a straight stitch 3 cm from the end with the small 6 cm Loop 	piece, anchoring the internal belt between both sides of the external belt.

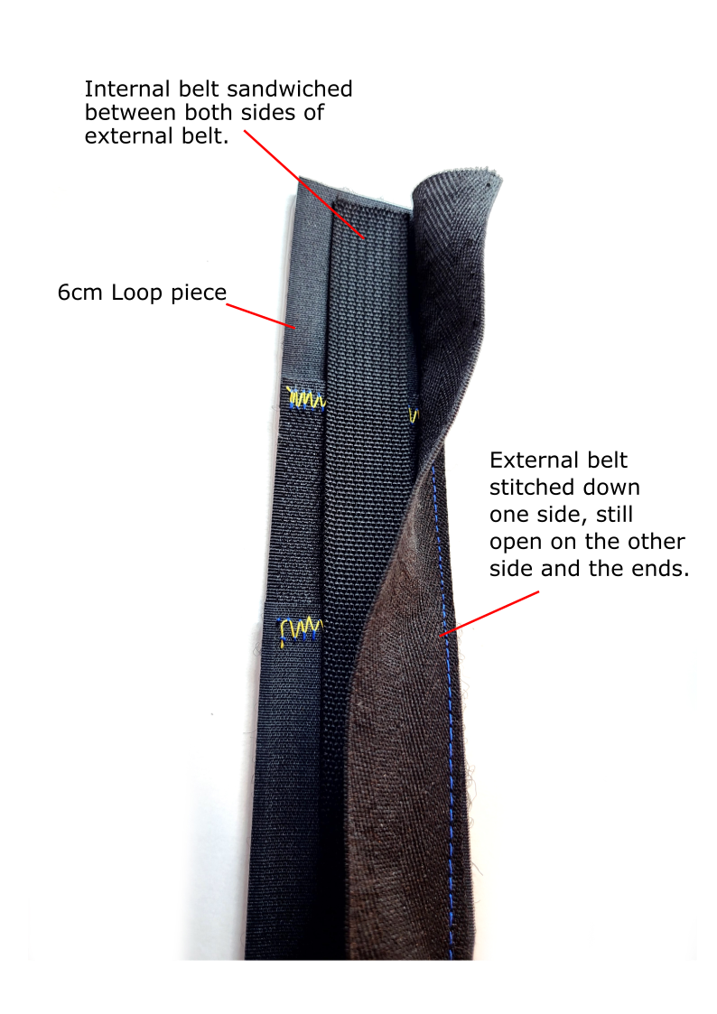
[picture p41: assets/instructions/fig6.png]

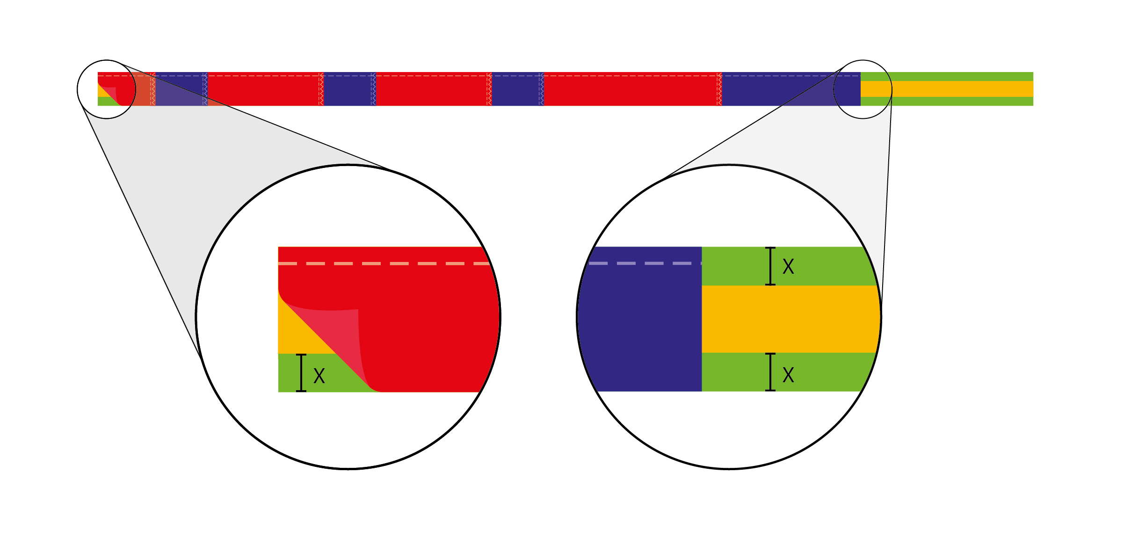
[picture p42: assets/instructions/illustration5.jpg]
Illustration 5

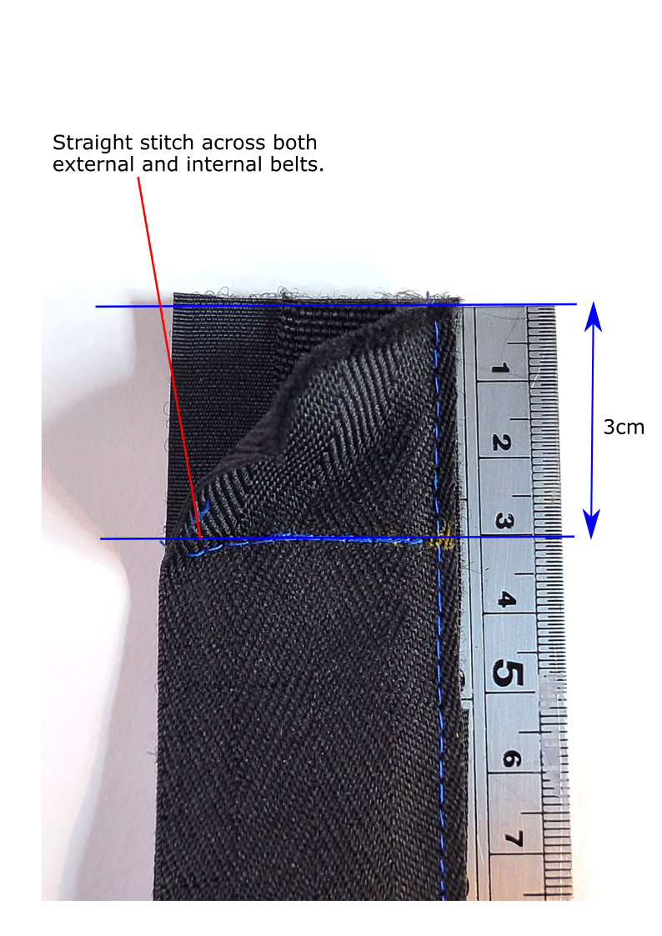
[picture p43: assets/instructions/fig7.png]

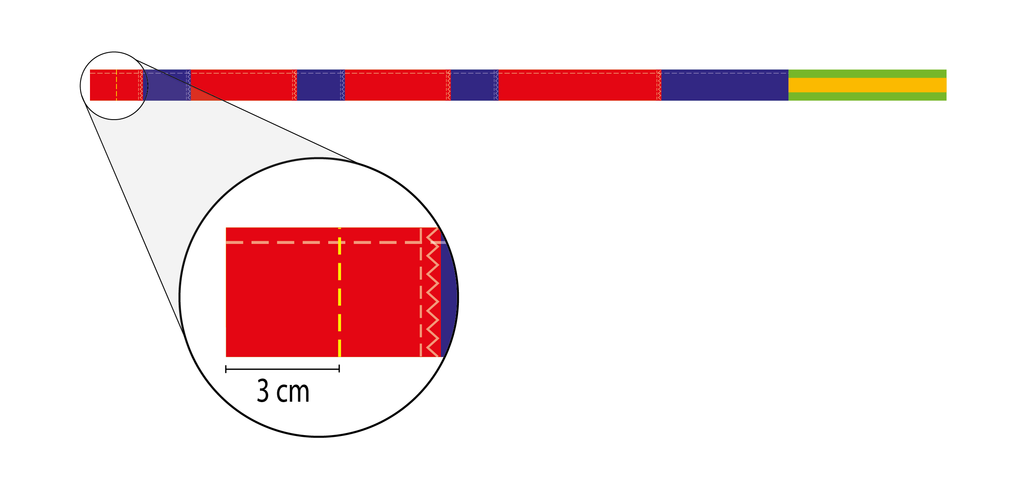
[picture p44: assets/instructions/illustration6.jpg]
Illustration 6


6. Sew box stitch 5 cm from end (2 cm from straight stitch across belts), then cut end round and 	sew around the cut edge. Carefully burn off frayed edge of belt.

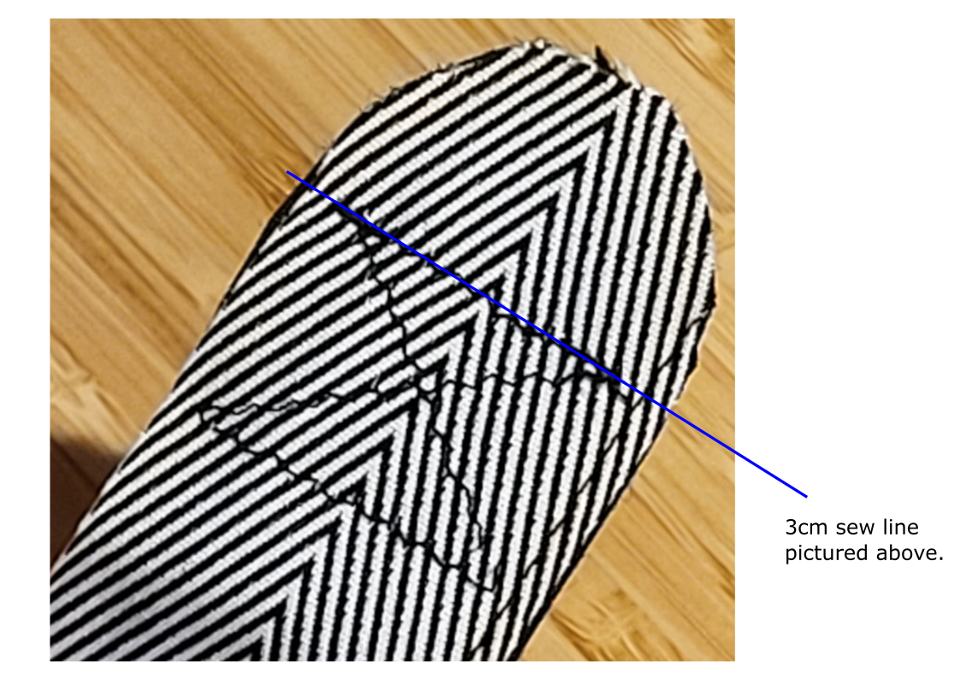
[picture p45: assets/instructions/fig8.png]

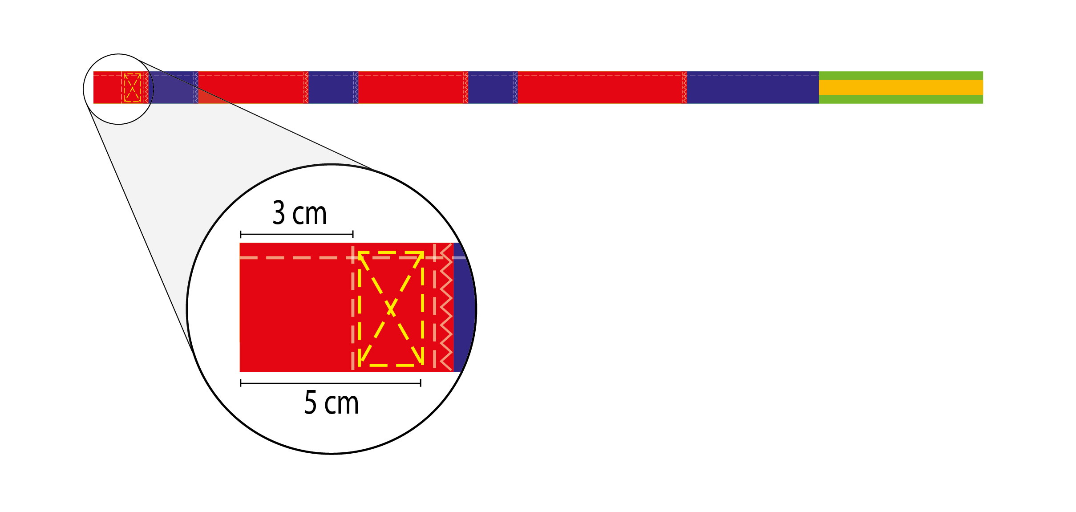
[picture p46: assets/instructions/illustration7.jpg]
Illustration 7

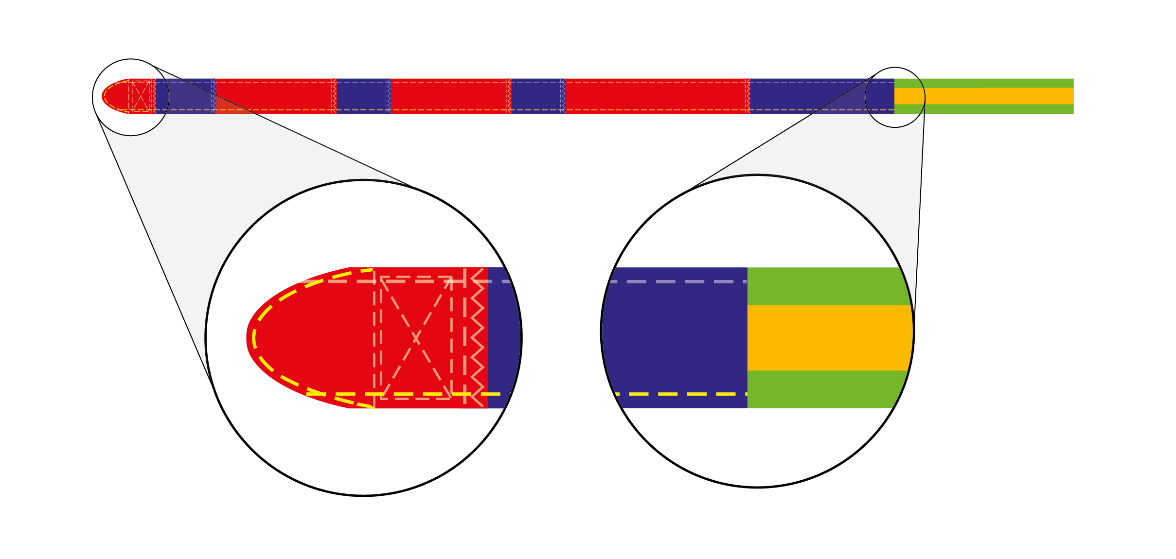
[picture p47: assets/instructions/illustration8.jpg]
Illustration 8


7. Sew the open side of the exterior belt making sure not to sew the side edge of the internal belt as well. **It is very important that the internal belt remains free to move.**

<p align="center">
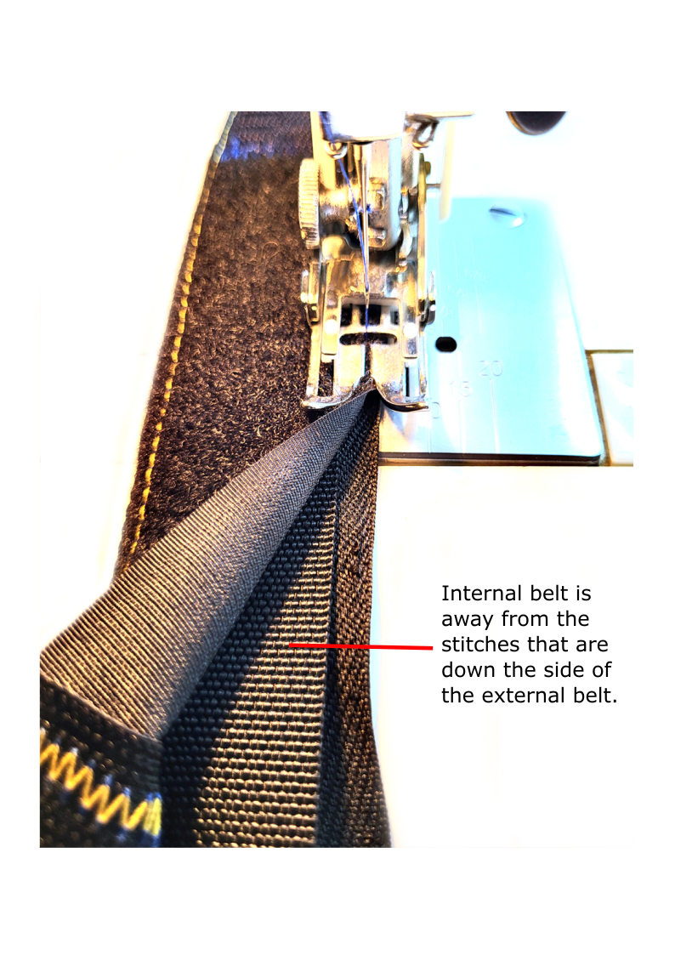
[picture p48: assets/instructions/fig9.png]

</p>

8. Insert only the internal belt through the slot in the 3d-printed windlass rod.

<p align="center">
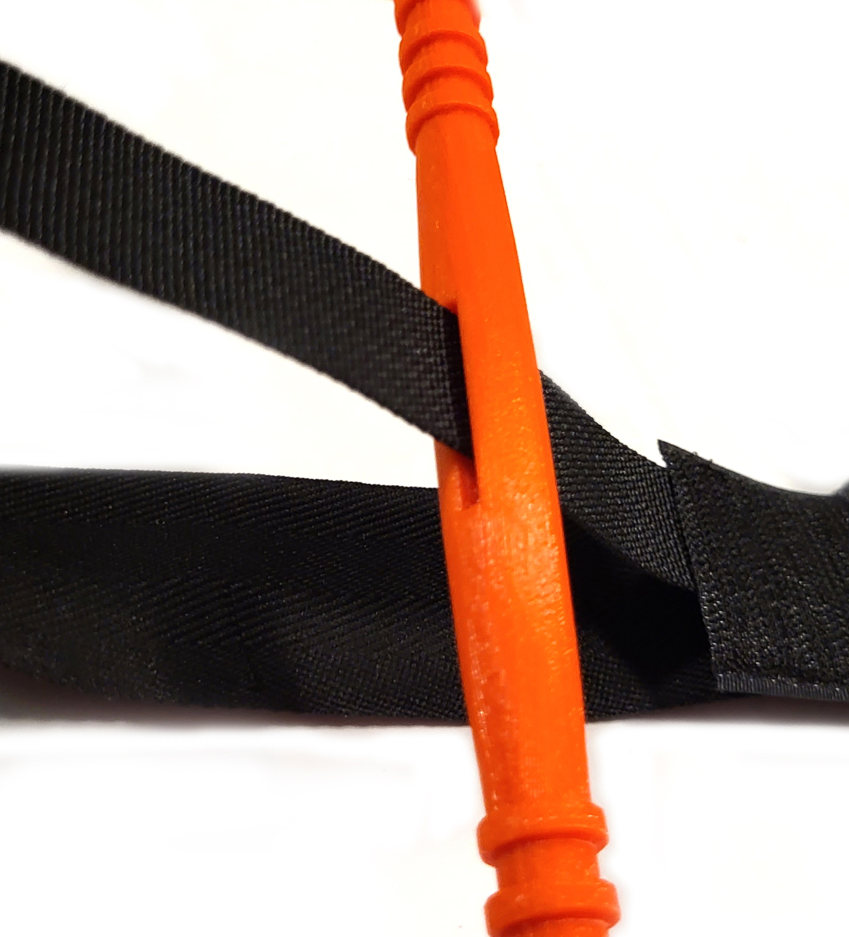
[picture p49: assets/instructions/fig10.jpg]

</p>

9. Then insert the internal and external belts through the slot on the back plate, ensuring the orientation of the back plate is 15mm under the 15cm hook piece (see photo at step 12).

<p align="center">
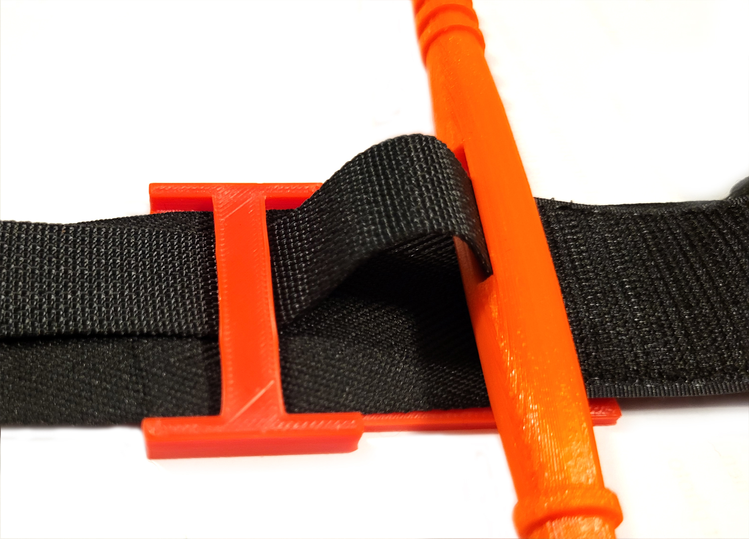
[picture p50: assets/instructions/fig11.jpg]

</p>

10. With the windlass in place, pull the internal belt up to 25 mm above the backing plate.

<p align="center">
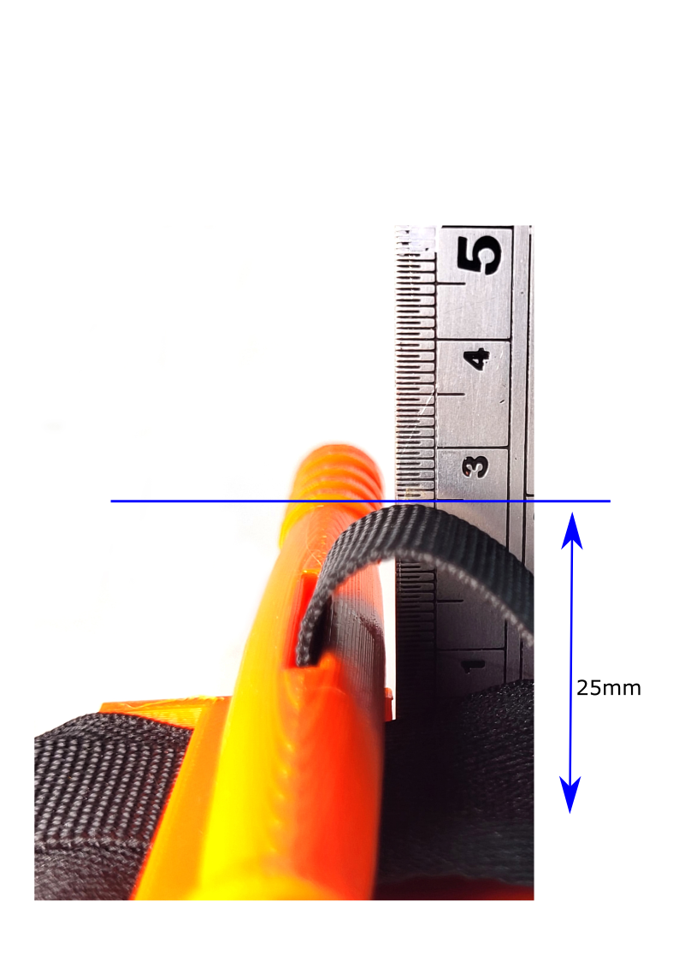
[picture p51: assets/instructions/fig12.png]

</p>

The [Strap Spacer](https://github.com/GliaX/tourniquet/blob/master/quality_control/strap_spacer.stl), found in the [quality_control](https://github.com/GliaX/tourniquet/blob/master/quality_control) folder, is a tool that can be used in order to ensure the inner strap has the correct slack needed.

<p align="center">
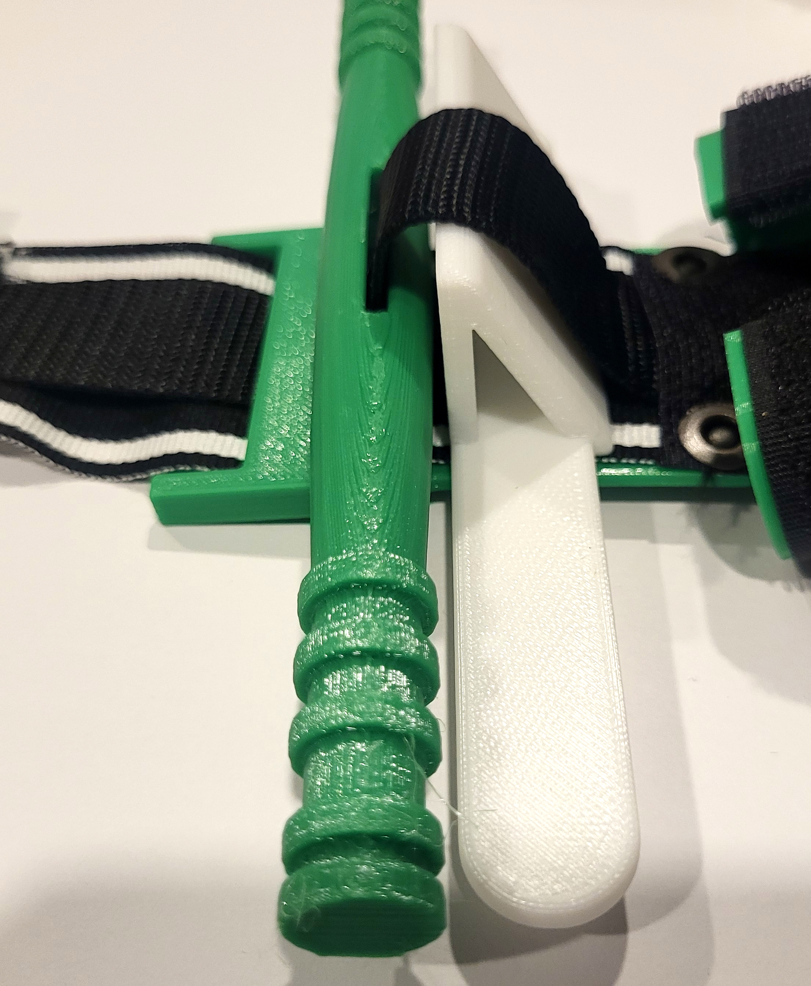
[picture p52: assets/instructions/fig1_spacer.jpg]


Insert the spacer under the inner strap with the slope side of the triangle facing away from the bridge of the backplate.
The windlass should be placed on top of the backplate, with the windlass hole facing upwards, between the bridge of the backplate and the spacer. 

The spacer should be flat on the outer strap. Pull the inner strap tight with the spacer in place, and this will set the appropriate slack of the inner strap. 

11. Insert the free end of the belts (both internal and external) through the toothless slot of the 3D printed buckle. Fold over and sew both internal and external belts to themselves 35 mm from the bridge of the back plate. **Back plate should be positioned 15mm under the 15cm hook piece (see step 12).**

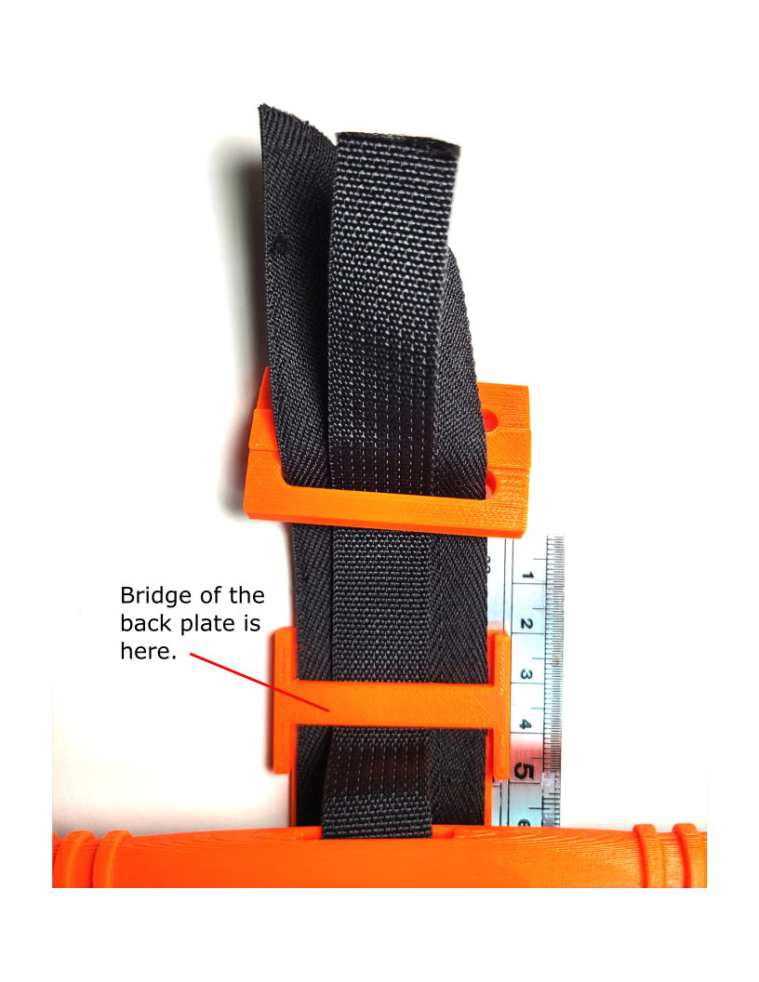
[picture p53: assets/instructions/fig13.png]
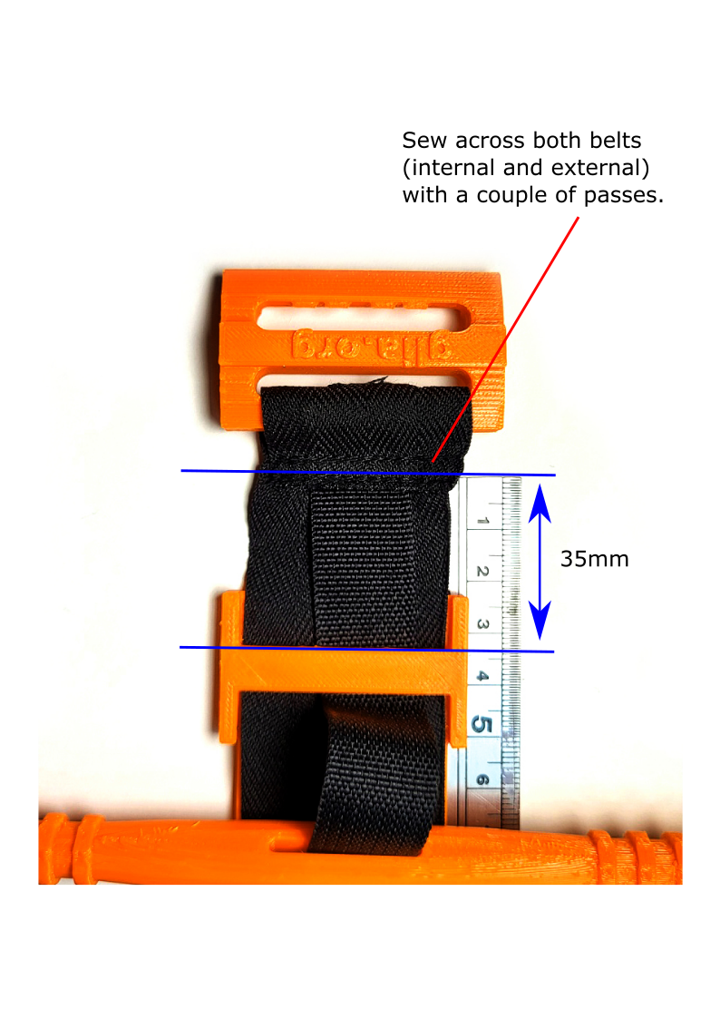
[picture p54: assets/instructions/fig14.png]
|||
|:--------------------------------------|:-------------------------|

12. Position edge of back plate under the piece of hook by 15 mm.

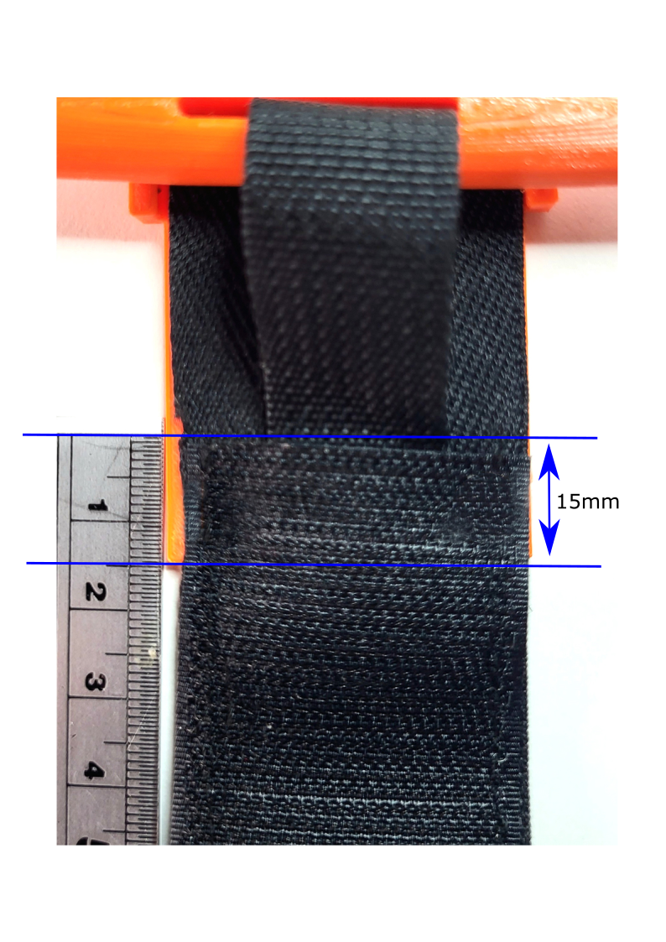
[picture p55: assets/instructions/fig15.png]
||
|:-------------------------|

13. Punch two holes through the external belt only **(avoid the internal belt)** where the holes are located on the back plate to mount it to the belt. Use a 7 mm head double cap rivet to fasten the back plate to the belt.

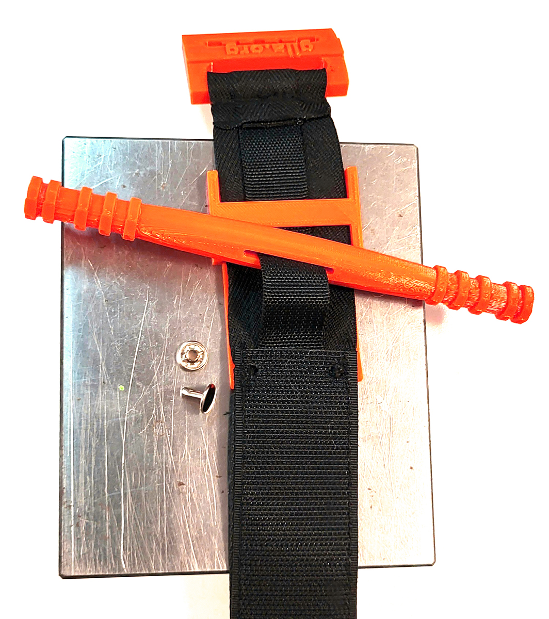
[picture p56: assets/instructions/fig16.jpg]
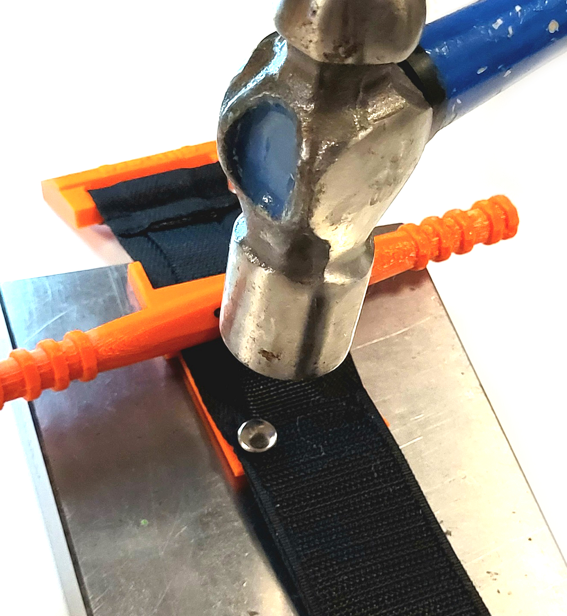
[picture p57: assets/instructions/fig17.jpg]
|||
|:--------------------------------------|:-------------------------|

14. Put the clip onto the belt. The clip is positioned so that the open end is always pointing toward the long end of the belt, **capped end toward the buckle**. Slide the 3D printed clip onto the belt by 	putting the belt down through slot 1 and up through slot 2, as shown below. Pull the clip along 	length of belt until it reaches the back plate and the belt is taught.

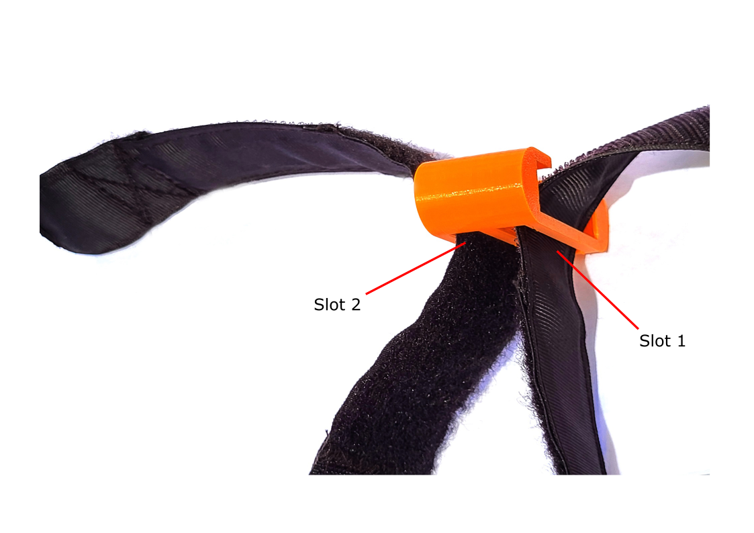
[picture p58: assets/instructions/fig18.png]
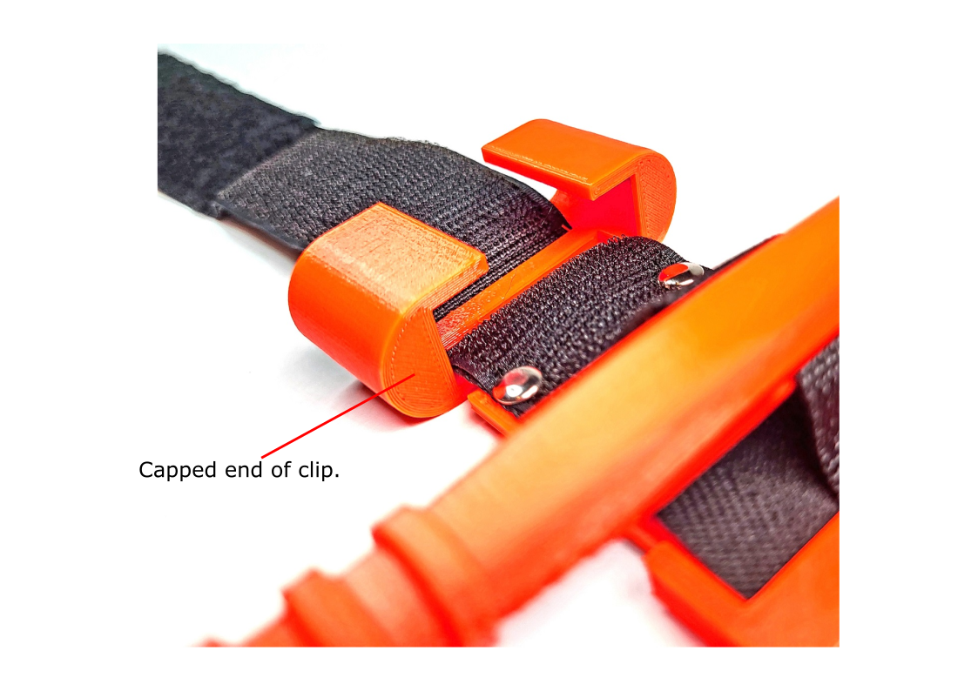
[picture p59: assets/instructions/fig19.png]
|||
|:--------------------------------------|:-------------------------|

15. To sew the Hoop and Loop assembly to be adhered to the clip, sew the end of the white non-adhesive Loop (face down) to the centre point of adhesive Hook (face up / black in the photo below).

<p align="center">
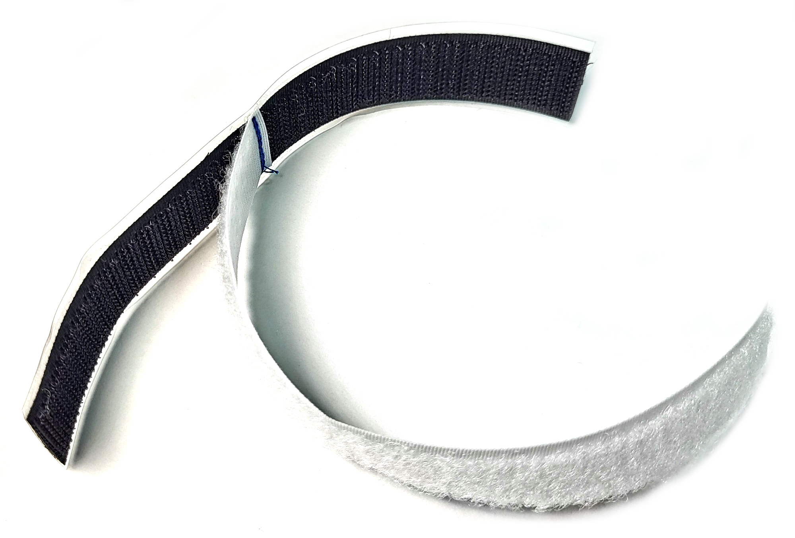
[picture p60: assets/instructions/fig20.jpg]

</p>

16. Adhere the Hook to the clip (Hook is black in the photos). **Use Cyanoacrylate (Super Glue) to permanently stick this piece onto clip if clip is printed with ABS. Use 90 second epoxy adhesive to stick if clip is printed in PETG.** Glue is applied as a dab under the open ends of the clip to glue the folded over ends of the Hook piece. Loop piece is free to wrap over top.

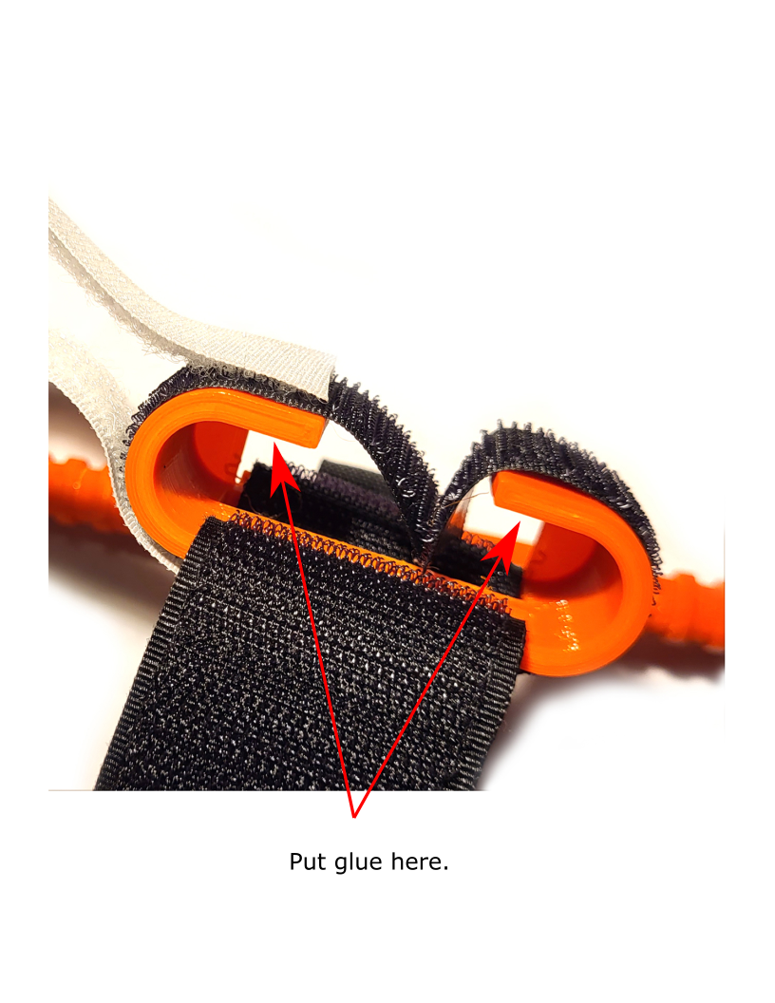
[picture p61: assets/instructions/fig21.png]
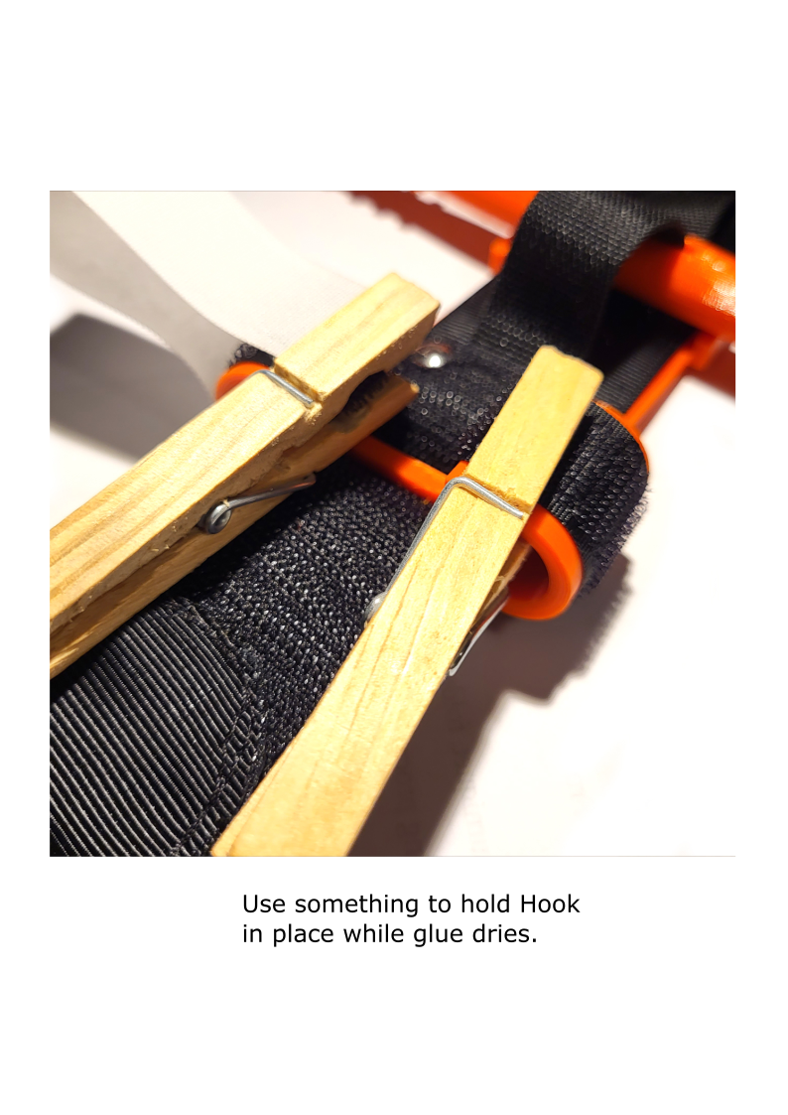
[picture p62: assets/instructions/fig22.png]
|||
|:--------------------------------------|:-------------------------|

17. To prepare for folding, position the white Loop piece same as in the photos below.

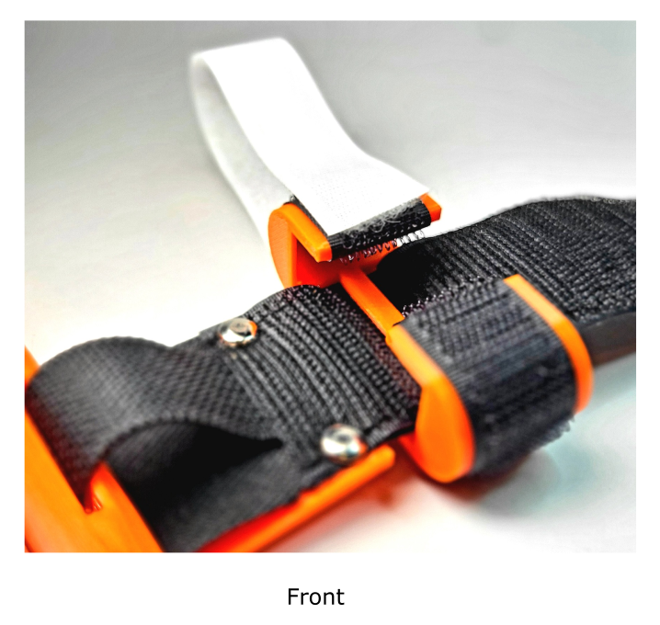
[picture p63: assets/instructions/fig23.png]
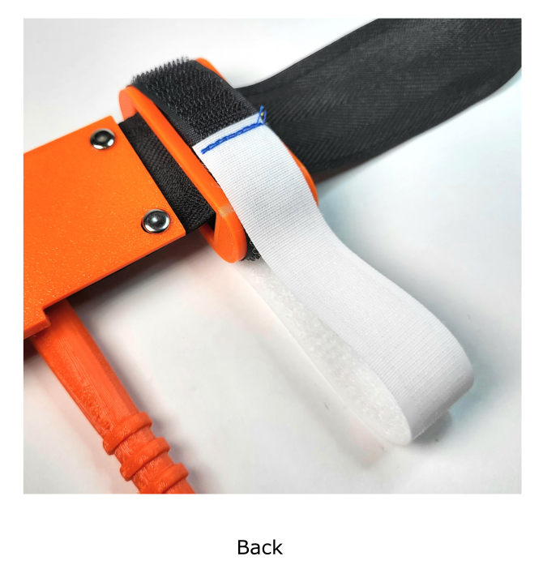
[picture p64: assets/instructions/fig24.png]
|||
|:--------------------------------------|:-------------------------|

18. Completed tourniquet, folded and ready for packaging. See folding video [here](https://www.youtube.com/watch?v=CSECJQPJmLw)

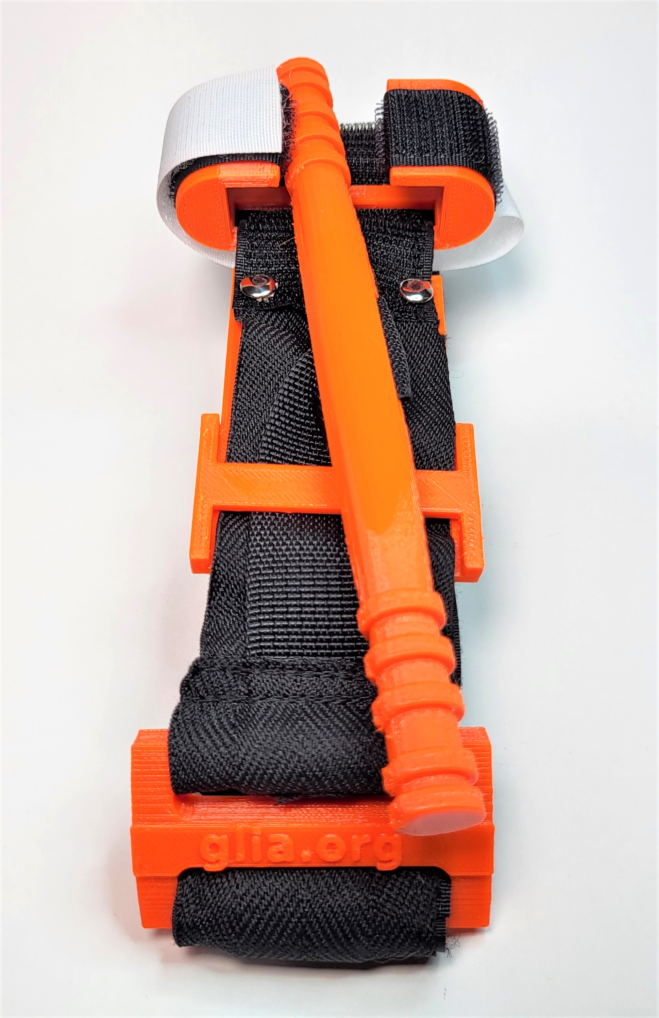
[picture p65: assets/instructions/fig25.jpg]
||
|:-------------------------|

*Note: You can use one Omni tape for the long belt instead of using separate parts of hook and loop (Velcro).*

# Troubleshooting
1. If you find it difficult to sew the velcro tapes together, first stick them onto a long piece of masking tape, then sew. Rip off the masking tape when done.  

2. Always make sure the internal belt is free to move after anchoring it at both ends. When turning the windlass, the internal belt should tighten.

3. The rivets should only be through the outer strapping. Make sure they are not through, or pinching, the internal belt.
  
4. Make sure the capped end of the clip is facing toward the buckle. This helps secure the windlass in place once it is turned to the appropriate tightness.
# Addendum
1) **Alternative Inner Belt Insertion**
<p>
*An alternative method of inserting the internal belt into the external belt (covering steps #4, 5, 6 and 7 in the Tourniquet Assembly Instructions).*

1(a). Sew the Hook and Loop belt to the 4cm external strapping down both long sides leaving both short ends open. This creates a tube in which the internal belt can be inserted into.

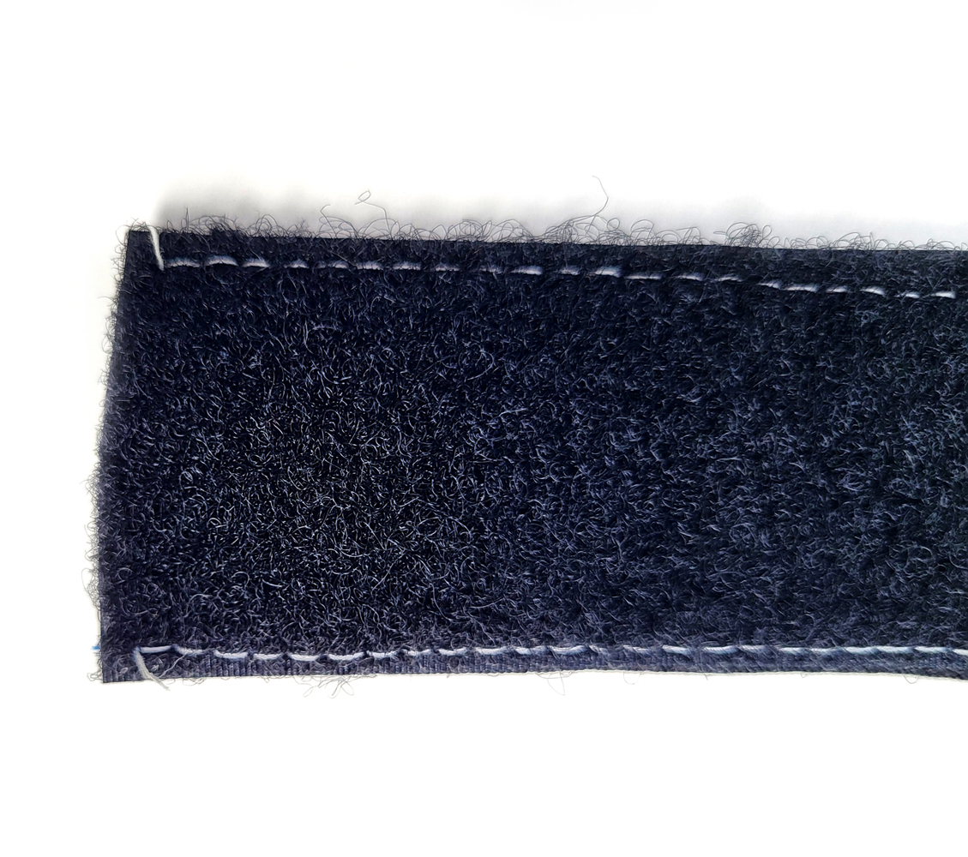
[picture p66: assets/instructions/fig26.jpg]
|||
|:--------------------------------------|:-------------------------|

1(b). Secure one end of the internal belt to one end of a rod that is the same length (or longer) than the internal belt.

||
|:-------------------------|
1(c). Insert that end into the external belt all the way until it comes out the other end. Then take the rod out leaving the internal belt inside the external belt.

|||
|:--------------------------------------|:-------------------------|

1(d). Sew across the internal and external belts with a straight stitch 3 cm from the end with the small Loop piece, anchoring the internal belt between both sides of the external belt, as in step #5 of the Tourniquet Assembly Instructions.

1(e). Continue with step #6 of the instructions, sewing a box stitch 5 cm from end (2 cm from straight stitch across belts), then cut end round and sew around the cut edge. Carefully burn off frayed edge of belt.

1(f). Skip step #7, and continue on with step #8 of the Tourniquet Assembly	Instructions.

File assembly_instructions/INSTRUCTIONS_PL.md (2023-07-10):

# Lista materiałów

|Czarna taśma rzepowa<br>NIESAMOPRZYLEPNA<br>o szerokości 3,8cm<br>na przednią część<br>paska zewnętrznego|Biała taśma rzepowa<br>SAMOPRZYLEPNA "pętelka"<br>i NIESAMOPRZYLEPNA "haczyk"<br>o szerokości 1,9cm<br>na zaczep|Czarna taśma rypsowa<br>o szerokości 3,8cm<br>i grubości 0,5mm<br>na tylną część<br>paska zewnętrznego|Wojskowa taśma poliamidowa<br>NIEROZCIĄGLIWA<br>o szerokości 1,9cm,<br>i grubości 1mm<br>na pasek wewnętrzny|
|:-------------------------|:-------------------------|:-------------------------|:-------------------------|
|Black self-adhesive hook and loop tape|White self-adhesive hook and loop tape|Polyester grosgrain strap|Nylon heavy webbing strap|

|Dwustronne<br>nity kaletnicze 7mm|Nić poliestrowa<br>w rozmiarze 40<br>|Cyjanoakrylat (Super Glue/Kropelka)<br>do ABS<br>klej epoksydowy dwuskładnikowy<br>do PETG|
|:-------------------------|:-------------------------|:-------------------------|
|Double cap rivet|thread|glue|

||
|:-------------------------|
<br>Instrukcje i szczegóły odnośnie drukowania części plastikowych do tej opaski zaciskowej znajdują się na profilu GitHub Glii pod linkiem:
https://github.com/GliaX/tourniquet

UWAGI:

1. Dla ścisłości instrukcji wyjaśniamy, że taśma rzepowa składa się z dwóch części. Sztywną i szorstką nazywamy "haczykiem", a miękką i pokrytą meszkiem nazywamy "pętelką". Rozróżnienie to jest bardzo ważne do prawidłowego przycięcia długości pasków.
2. Wahania szerokości pasków o 1-2mm nie mają znaczenia jeśli tylko paski zewnętrzne (rzepowy i rypsowy) nie mają większej szerokości niż 4cm i pasek wewnętrzny nie większą szerokość niż 25mm.
3. W instrukcji posługujemy się następującym nazewnictwem odnośnie części opaski wydrukowanych w technologii 3D: drążek (oryg. windlass), płytka (oryg. backplate), zaczep (oryg. clip) i klamerka (oryg. buckle).  

# Instrukcja montażu
1. Potnij wszystkie paski i rzepy na kawałki o długościach wyszczególnionych w tabeli:

|Materiał|Ilość|Długość|
|:--------------------------------------|:-------------------------|:-------------------------|
|Czarny rzep niesamoprzylepny "haczyk" szerokości 3,8cm|3|6cm|
|Czarny rzep niesamoprzylepny "haczyk" szerokości 3,8cm|1|15cm|
|Czarny rzep niesamoprzylepny "pętelka" szerokości 3,8cm|1|6cm|
|Czarny rzep niesamoprzylepny "pętelka" szerokości 3,8cm|2|12.5cm|
|Czarny rzep niesamoprzylepny "pętelka" szerokości 3,8cm|1|19cm|
|Czarna taśma rypsowa szerokości 3,8cm|1|92cm|
|Wojskowa taśma poliamidowa szerokości 1,9cm |1|95cm|
|Biały rzep samoprzylepny "haczyk" szerokości 1,9cm|1|16cm|
|Biały rzep niesamoprzylepny "pętelka" szerokości 1,9cm|1|17cm|
Illustration 1
<p>
<p>
*Na rysunku oznaczone są: Loop ("pętelka"), Hook ("haczyk"), Nylon Heavy Webbing Strap (wojskowa taśma poliamidowa), Polyester Cotton Webbing Strap (taśma rypsowa). Długości dwóch ostatnich ustalone są na 97cm (niezgodnie z tabelą). Jest to zabieg celowy zwiącany z tym, że kanadyjski oddział Glii stara się produkować swoje paski w myśl idei zero waste. Długości zaznaczone w tabeli pozwalają uszyć pasek pozostawiając mniej ścinków, które potem trzeba wyrzucić. Na początku można jednak zacząć od dłuższych pasków o długości 97cm, gdyż będą one łatwiejsze do uszycia.*
<p>
<p>
2. Aby uszyć przednią część paska zewnętrznego, najpierw ułóż przycięte paski według długości kolejno: 6cm "pętelka", 6cm "haczyk", 12,5cm "pętelka", 6cm "haczyk", 12,5cm "pętelka", 6cm "haczyk", 9cm "pętelka" i 15cm "haczyk". Kolejność ułożenia pasków pokazana jest na zdjęciu, pierwszy kawałek do zszycia to 6cm "pętelki" i 6cm "haczyka".   

||
|:-------------------------|

3. Zszywaj kawałki kaskadowo, czyli wkładając każdy kolejny kawałek pod spód poprzedniego. Przeszyj ten sam szew kilka razy ściegiem zygzakowym. Kawałki pasków powinny nachodzić na siebie na około 1cm i szew powinien przechodzić przez środek tego nachodzenia, a nie na krawędzi paska. Ten rodzaj szycia zwiększa wytrzymałość na rozciąganie paska i umożliwia bezproblemowe przeciągnięcie go przez klamerkę. Gotowy pasek rzepowy będzie miał około 76cm długości.


Illustration 2
Illustration 3

4. Do właśnie uszytego paska z rzepów przyszyj pasek rypsowy (3,8cm) ściegiem prostym upewniając się uprzednio, że czepliwa strona rzepów skierowana jest na zewnątrz. Na razie zszyj tylko jedną stronę, drugą pozostaw, by pomiędzy paskami umieścić wewnętrzny pasek z wojskowej taśmy poliamidowej. (Alternatywna metoda umieszczania paska wewnętrznego znajduje się w dodatkowych informacjach pod instrukcją montażu.)



Illustration 4

5. Umieść pasek wewnętrzny (1,9cm) w przerwie pomiędzy taśmą rypsową i paskiem z rzepów i przeszyj cały pasek prostopadle ściegiem prostym w ogległości około 3cm od krawędzi paska która zaczyna się 6-ścio centymetrowym kawałkiem rzepu "pętelki". Ma to na celu zamocowanie wewnętrznego paska w środku i przez to ułatwienie dalszego szycia.


Illustration 5

Illustration 6

6. Naszyj wzmacniający ścieg w kształcie prostokąta z iksem około 5cm od krawędzi paska (2cm od właśnie przeszytego prostopadłego ściegu), następnie przytnij krawędź na okrągło i wykończ zapalniczką ostrożnie przypalając postrzępione nitki.


Illustration 7
Illustration 8

7. Zaszyj otwartą częśc paska uważając, by w trakcie tej czynności nie przeszyć paska wewnętrznego. **Pasek wewnętrzy bezwzględnie musi pozostać ruchomy!**

<p align="center">

</p>

8. Przełóż sam wewnętrzny pasek przez otwór w wydrukowanym 3D drążku.

<p align="center">

</p>

9. Następnie przełóż zewnętrzny i wewnętrzny pasek przez otwór w płytce, upewniając się, że płytka umiejscowiona jest 15mm pod kawałkiem "haczyka" o długości 15cm (jak na zdjęciu przy punkcie 12. instrukcji).

<p align="center">

</p>

10. Umieść drążek na żeberku płytki i wyciągnij wewnętrzny pasek, tak by wystawał na około 25mm do góry, mierząc od powierzchni płytki.

<p align="center">

</p>

11. Wolne końce pasków (wewnętrznego i zewnętrznego) przeciągnij przez otwór wydrukowanej 3D klamerki pozbawiony "ząbków". Obróć opaskę na drugą stronę i przeszyj paski razem w odległości 35mm od mostka płytki. **Płytka powinna być usytuowana 15mm pod kawałkiem 15cm rzepu "haczyka" (patrz punkt 12. instrukcji)**

|||
|:--------------------------------------|:-------------------------|

12. Ustaw płytkę pod kawałkiem rzepowego "haczyka" w odległości 15mm od jego krawędzi.

||
|:-------------------------|

13. Przebij dwie dziurki przez sam pasek zewnętrzny **(nie naruszaj paska wewnętrznego)** w miejscu otworów na płytce. Za pomocą 7mm nitów kaletniczych zamocuj płytkę do paska przez właśnie zrobione dziurki.

|||
|:--------------------------------------|:-------------------------|

14. Załóż zaczep na pasek. Zaczep jest usytuowany w taki sposób, że jego otwarta część zawsze skierowana jest w stronę dłuższego końca paska, **a druga strona z pokrywką skierowana jest w stronę klamerki**. Przełóż pasek przez wydrukowany 3D zaczep w dół otworu 1 (slot 1) i w górę otworu 2 (slot 2), jak na zdjęciu poniżej. Przeciągnij klip przez całą długość paska aż oprze się o płytkę.

|||
|:--------------------------------------|:-------------------------|

15. Aby uszyć mocowanie na drążek, weź pozostałe kawałki węższego rzepa 1,9cm i przyszyj jeden z końców białego niesamoprzylepnego rzepa "pętelki" do punktu na środku samoprzylepnego czarnego rzepa "haczyka" (czepliwa strona obu rzepów musi być skierowana w górę, jak na zdjęciu poniżej).

<p align="center">

</p>

16. Przyklej mocowanie do zaczepu w taki sposób, by czarny rzep "haczyk" oplatał go całkowicie dookoła i zawijał się do spodu. **Użyj cyjanoakrylatu jeśli zaczep został wydrukowany z ABS i żywicy dwuskładnikowej, jeśli zaczep został wydrukowany z PETG** Klej należy nałożyć w niewielkiej ilości od spodu pałąka i następnie zawinąć wolne końce rzepu "haczyka". Rzep "pętelka" pozostaje wolny, tak by dało się go swobownie owinąć na pałąku zaczepu.

|||
|:--------------------------------------|:-------------------------|

17. Aby przygotować opaskę do składania, usytuuj biały rzep "pętelkę" jak na zdjęciu poniżej.

|||
|:--------------------------------------|:-------------------------|

18. Gotowa opaska uciskowa, złożona i gotowa do pakowania. Zobacz nagranie z instrukcją składania [tutaj](https://www.youtube.com/watch?v=CSECJQPJmLw)

||
|:-------------------------|

*Uwaga: Podczas szycia paska zamiast naprzemiennego szycia kawałków "haczyków" i "pętelek" możesz użyć paska Omnitape, czyli rzepu, który na jednej stronie ma zarówno haczyki i pętelki przez co potrafi się przyczepić sam do siebie.*

# Rozwiązywanie problemów
1. Jeśli masz problem ze zszywaniem razem pasków rzepa, spróbuj najpierw nakleić kawałki na długi kawałek taśmy maskującej, przeszyć je razem i na końcu usunąć taśmę.

2. Zawsze upewniaj się, że pasek wewnętrzny może poruszać się swobodnie wewnątrz opaski po zszyciu obu jej końców. Przy obracaniu drążkiem, pasek wewnętrzny powinien się zacieśniać.

3. Nity kaletnicze powinny przechodzić jedynie przez pasek zewnętrzny. Upewnij się, że nity nie przechodzą przez pasek wewnętrzny ani go nie przyszczypują.
  
4. Upewnij się, że zabudowana strona zaczepu (z pokrywką) jest skierowana w stronę klamerki. Umożliwi to poprawne zamocowanie drążka i utrzymanie odpowiedniego ucisku.

# Dodatkowe informacje 
1) **Alternatywna metoda umieszczania paska wewnętrznego w opasce**
<p>
*Alternatywna metoda umieszczania paska wewnętrznego w opasce (zamiast kroków 4., 5., 6. i 7. w instrukcji montażu opaski uciskowej.*

1(a). Przyszyj wzdłuż dłuższej krawędzi taśmę rzepową uszytą z kawałków "haczyka" i "pętelki" do taśmy rypsowej o szerokości 3,8cm pozostawiając oba końce paska otwarte, tak by dało się przez nie przeciągnąć pasek wewnętrzny.

|||
|:--------------------------------------|:-------------------------|

1(b). Zamocuj jeden koniec paska wewnętrznego do końca wąskiego kijka, o takiej samej lub większej długości od paska wewnętrznego.

||
|:-------------------------|
1(c). Wsuń koniec kijka z zamocowanym paskiem wewnętrznym do paska zewnętrznego przez całą jego długość, aż pokaże się z drugiej strony, następnie odczep od kijka pasek wewnętrzny i wyciągnij kijek z paska zewnętrznego, pozostawiając pasek wewnętrzny w środku.

|||
|:--------------------------------------|:-------------------------|

1(d). Wykonaj ścieg prostopadle do dłuższej krawędzi paska przez wszystkie jego warstwy w odległości 3cm od końca kawałka 6cm "pętelki", zaczepiając tym samym pasek wewnętrzny pomiędzy warstwami rzepa i taśmy rypsowej, jak w punkcie 5. instrukcji montażu opaski uciskowej.

1(e). Kontynuuj od kroku 6. instrukcji, wykonując prostokątny ścieg z iksem w odległości 5 cm od końca paska (2cm od właśnie wykonanego ściegu prostopadłego). Następnie przytnij krawędź na okrągło i ostrożnie przypal odstające nitki zapalniczką.

1(f). Pomiń krok 7. i kontynuuj od kroku 8. instrukcji montażu opaski uciskowej.

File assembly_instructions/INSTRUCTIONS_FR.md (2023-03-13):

# Nomenclature des matériaux
* Bande auto-agrippante noire (Velcro) [largeur 3,5-3,85 cm] pour la face avant de la ceinture.
* Bande auto-agrippante blanche (Velcro) [largeur 3,5-3,85 cm] pour la sangle du clip du guindeau.
* Sangle en toile de coton polyester [largeur 3,5-3,85 cm] pour la face arrière de la ceinture.
* Sangle en nylon résistant non extensible [largeur de 2,5 cm] pour la ceinture interne.
* Rivets avec double bouchon 7mm tête.
* Fil polyester [épaisseur 0,75 mm].
* Colle cyanoacrylate (Super glue).
* Composants imprimés en 3D.

Black self-adhesive hook and loop tape
White self-adhesive hook and loop tape
Polyester cotton webbing strap
Nylon heavy webbing strap
Double cap rivet
Omni tape

# Instructions de montage
1. Coupez toutes les sangles et les pièces auto-agrippantes (Velcro) aux longueurs requises.
 * Crochet et boucle noirs (Velcro) (Crochet : 3 pièces de 6 cm chacune et une pièce de 15 cm de longueur, boucle : une pièce de 6 cm, deux pièces de 12,5 cm, une pièce de 19 cm)
 * Ruban auto-adhésif blanc à boucles et crochets (crochet : 20 cm, boucle : 20 cm) une pièce pour chacune
 * Sangle en toile de coton polyester (une pièce 97 cm)
 * Sangle en nylon épais (une pièce de 97 cm)


Illustration 1

2. Pour la face avant de la ceinture, cousez les morceaux de crochet et de boucle (Velcro) ensemble dans l'ordre [boucle de 6 cm, crochet de 6 cm, boucle de 12,5 cm, crochet de 6 cm, boucle de 12,5 cm, crochet de 6 cm, boucle de 19 cm, crochet de 15 cm]. Superposez chaque pièce de 1 cm et cousez sur chaque joint de connexion en deux passes pour une résistance à la traction accrue.

Illustration 2
Illustration 3

3. Cousez le crochet et la boucle (Velcro) sur le morceau de sangle pour la face arrière. Cousez les deux ensembles sur toute la longueur d'un côté. Laissez l'autre côté et les extrémités ouvertes pour insérer la ceinture interne.

Illustration 4

4. Placez la ceinture interne entre la sangle auto-agrippante (Velcro) et la face arrière. Amenez la pointe des trois pièces au ras d'une extrémité. Cousez sur la largeur à 3 cm de l'extrémité pour que la ceinture interne soit ancrée aux deux pièces externes. Cousez un motif en « X » du point précédent à 3 cm jusqu'à un point à 5 cm.

Illustration 5
Illustration 6
Illustration 7

5. Coupez la pointe en forme arrondie et cousez la ceinture fermée sur toute la longueur. Lors de la couture des deux faces extérieures, il est très important que la ceinture intérieure reste libre de ses mouvements et ne soit pas coincée le long des coutures latérales.

Illustration 8

6. Percez ou cognez deux trous à travers l'ensemble de la ceinture à l'extrémité d'une pièce de crochet et de boucle (Velcro) de 15 cm pour monter la plaque de support imprimée en 3d. La sangle auto-agrippante (Velcro) se chevauchera sur la plaque de support de 15 mm.

Illustration 9

7. Utilisez un rivet à double capuchon pour fixer la plaque de support à la ceinture à travers les deux trous.




8. Insérez la pointe de la ceinture cousue dans la fente du clip imprimé en 3D jusqu'à ce qu'elle atteigne le support arrière. Tenez compte de garder l'extrémité fermée du clip vers la plaque de support.



9. Insérez la ceinture interne dans la fente de la tige de guindeau imprimée en 3d, puis dans la fente du support arrière avec la sangle restante.



10. Avec le guindeau en place, reprenez le mou de la ceinture ou de la sangle.

11. Pour insérer l'extrémité libre de la ceinture à travers la fente sans dents de la boucle imprimée en 3d, insérez vers le haut à travers la fente puis repliez-la sur elle-même. La boucle doit reposer à environ 3 cm du bord de la plaque de support. Cousez la sangle avec quelques passages. Coupez tout matériau supplémentaire.



12. Retirez tous les fils supplémentaires pour nettoyer les bords.

13. Assurez-vous que l'extrémité arrondie de la ceinture est cousue fermée.



14. Cousez l'extrémité du crochet blanc au point central de la boucle blanche pour faire la sangle du clip du guindeau.



15. Utilisez de la super glue pour fixer la sangle du guindeau sur le clip du guindeau. Le morceau de crochet restera libre pour s'enrouler sur le dessus. Super glue est à  utiliser sur l'ABS.



* Remarque : vous pouvez utiliser une bande Omni pour la ceinture longue au lieu d'utiliser des parties séparées de crochet et de boucle (Velcro).

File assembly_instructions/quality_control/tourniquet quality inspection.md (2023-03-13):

# Quality inspection of Glia Tourniquets
This document is revision: **A**

## Revision history

|Revision|Changes from previous revision|
|---|---|
|A | Initial creation of document|

## Purpose

This document contains the quality inspection characteristics and methods of inspection. In other words, what things need to be inspected and how to inspect those things.

## Inspection characteristics

### IC-0010 (Sewing complete)
|Method of inspection|Tools required for inspection|
|---|---|
|Visual inspection|None|

All sewing must be complete. All loose threads must be removed.

### IC-0020 (Round end of strap heat sealed)
|Method of inspection|Tools required for inspection|
|---|---|
|Visual inspection|None|

The round end of the strap must be heat sealed.

IC-0020A1 End of strap heat sealed

### IC-0030 (Rivets installed)
|Method of inspection|Tools required for inspection|
|---|---|
|Visual inspection|None|

Both rivets are installed and secure.

IC-0030A1 Rivets in place from top
IC-0030A2 Rivets in place from bottom

### IC-0040 (Clip orientation)
|Method of inspection|Tools required for inspection|
|---|---|
|Visual inspection|None|

The clip is installed with the "capped" end towards the windlass and buckle and the "open" end facing away.

IC-0040A1 Clip oriented with capped ends towards windlass

Note: the capped ends are there to provide strength to the clip. They are NOT supposed to "cover" the windlass when it is secured. The windlass will stick out thru the open end of the clip when properly secured during application to an extremity.

IC-0040A1 Clip oriented with capped ends towards windlass and windlass clipped in

### IC-0050 (Measurement from back plate to windlass slot)
|Method of inspection|Tools required for inspection|
|---|---|
|Length measurement|Ruler OR more accurate device|

The distance between the backing plate and the windlass slot must 25mm +/- 2mm.

IC-0050A1 measurement between back plate and windlass slot

### IC-0060 (Measurement of bridge of back plate to buckle stitching)
|Method of inspection|Tools required for inspection|
|---|---|
|Length measurement|Ruler OR more accurate device|

The distance between the bridge of the back plate and stitching that secures the buckle must be 30mm +/- 2mm.

IC-0050A1 measurement between the back plate and the stitching that secures the buckle

### IC-0070 (Routing of strap thru buckle slot, orientation of buckle)
|Method of inspection|Tools required for inspection|
|---|---|
|Visual inspection|None|

The buckle must be oriented with the strap run thru the plain "open" side. The toothed "gripper" side of the buckle must be at the end of the tourniquet.

IC-0070A1 Strap routed thru the buckle

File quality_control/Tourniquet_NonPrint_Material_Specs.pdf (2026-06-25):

### TOURNIQUET Non-Printed Material Specs

Sewing Material | Specs
3/4” nylon webbing https://jtsoutdoorfabrics.com/black_nylon_webbing (https://jtsoutdoorfabrics.com/black_nylon_webbing) | Break Strength is estimated at: 3/4" - 745 lbs 100% Nylon Fibers, 840 Denier. Standard Heat and UV Radiation stabilized. Catch cord applied. Yarn Count: Warp: 840 D Weft: 210 D Passes Motor Vehicle Safety Standard 302 Fire Code Thickness: 1.1 mm
1.5” nylon hook and loop tape https://jtsoutdoorfabrics.com/Economical-Nylon-Loop-Tape--Black--82-Roll_p_17017.html (https://jtsoutdoorfabrics.com/Economical-Nylon-Loop-Tape--Black--82-Roll_p_17017.html) | Content: 100% Nylon Peel Cleavage: 2.5 N/cm Shear: 10 N/sq cm Shrinkage: Less than 2% Strength:Above 250 N/cm Temperature: Melting temperature: Above 200 degrees Celsius Thickness: 2mm

### 1.5” grosgrain ribbon

### https://ribbonfactory.com/store/ display_item/646.html (https://ribbonfactory.com/store/display_item/646.html)

Fiber: 100% Polyester (PET)

- Properties: Synthetic fiber provides high dimensional stability, excellent resistance to shrinking/stretching, and good elasticity recovery. It is naturally resistant to mildew, moths, and most household chemicals.

Weave Type: Grosgrain (a heavy-weft variation of the plain/standard weave)

- Construction: Achieved by alternating a thick, dominant weft (crosswise) yarn with finer warp (lengthwise) yarns. This creates the characteristic transverse ribs running perpendicular to the ribbon's length.
- Density: Tightly woven with a high thread count, resulting in a dense, opaque structure with a stiff, crisp hand.

Tensile Strength: Medium-to-high for a decorative ribbon. The polyester fibers and tight ribbed weave provide good load distribution, though exact break strength varies by width (typically estimated at 15–40 lbs of force for a 1½" width depending on yarn denier).

- Elongation at Break: Low (~3–5%). The minimal stretch ensures the ribbon holds its shape under tension but does not absorb shock like elastic or nylon webbing.
- Friction & Hardware Grip: The ribbed surface offers moderate friction, but it is not engineered to grip buckles or friction-fit hardware under high tension. Unlike industrial webbing, the flat plain-weave structure cannot lock onto fasteners.
- Fray Resistance: High. The heavy weft ribs and synthetic fiber prevent edges from unraveling, even when cut without heat sealing.


### 9.5mm jean ring rivets (brass)

### https://www.micronamerica.com/ product/9-5mm-ring-rivets-100-sets/ (https://www.micronamerica.com/product/9-5mm-ring-rivets-100-sets/)

### T = 9.5 mm

### H = 2.7 mm

### S = 4.6 mm


### T = 9.5 mm

### H = 8.3 mm

### S = 2.5 mm

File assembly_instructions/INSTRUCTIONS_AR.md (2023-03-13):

# قائمة المواد اللازمة لصناعة حزام وقف النزيف
* ‏شريط لصق ذاتي (فلكرو) أسود[ عرض 3.5 - 3.85 سم ] للجزء الأمامي من الحزام
* ‏شريط لصق ذاتي (فلكرو) أبيض[عرض 2 سم ] للمشبك.
* ‏حزام من القطن والبوليستر[ عرض 3.5 - 3.85 سم ] للجزء الخلفي من الحزام.
* ‏حزام سميك من النايلون[ عرض 2.5 سم ] للحزام الداخلي.
* ‏برشام.
* ‏خيوط بوليستر [سماكة 0.75 ملم ] للخياطة أجزاء الحزام.
* ‏غراء قوي.








* ملاحظة: يمكن استخدام قطعة واحدة من شريط اللصق الذاتي (Omni tape) بدلاً من استخدام أجزاء منفصلة من شريط فلكرو

# ‏خطوات العمل
1. قص الأحزمة بالأطوال المطلوبة، وهي على النحو الآتي:
 * شريط لصق ذاتي (فلكرو) أسود (الجزء الخشن: 3 قطع بطول 6 سم لكل منهم وقطعة واحدة بطول 15 سم، الجزء الناعم: قطعة واحدة بطول 6 سم وقطعتين بطول 12.5 سم وقطعة واحدة بطول 19 سم).
 * شريط لصق ذاتي (فلكرو) أبيض (الجزء الخشن: قطعة واحدة بطول 20 سم، الجزء الناعم: قطعة واحدة بطول 20 سم).
 * حزام من القطن والبوليستر (قطعة واحدة بطول 97 سم).
 * حزام سميك من النايلون (قطعة واحدة بطول 97 سم).


Illustration 1

2. لتشكيل الجزء الأمامي من الحزام، قم بخياطة أشرطة اللصق الذاتي (فلكرو) السوداء التي أعدتها مع بعضها البعض بالتسلسل التالي[ 6 سم ناعم، 6 سم خشن، 12.5 سم ناعم، 6 سم خشن، 12.5 سم ناعم، 6 سم خشن، 19 سم ناعم، 15 سم خشن ].
مع الأخذ بالحسبان ضرورة تكرار عملية الخياطة لتقوية الحزام وتكون عملية دمج القطع ببعضها من خلال جعل طرف كل قطعة فوق طرف القطعة التي تليها لتسهيل عملية شد الحزام.

Illustration 2
Illustration 3

3. قم بخياطة الجزء الأمامي من الحزام مع الجزء الخلفي من جانب واحد فقط، اترك الجانب الآخر مفتوحاً لإدخال الحزام الداخلي.

Illustration 4

4. قم بإدخال الحزام الداخلي بين الجزء الأمامي والجزء الخلفي من الحزام ثم قم بخياطة طرف الحزام مع الحزامين الأمامي والخلفي ثم كرر هذه العملية أكثر من مرة بحيث تكون الخياطة بشكل متعرج (zig-zag) وحتى 5 سم من طرف الحزام.

Illustration 5
Illustration 6
Illustration 7

5. قم بخياطة الجزء الأمامي من الحزام مع الجزء الخلفي من الجانب الآخر مع الأخذ بالحسبان أن يكون الحزام الداخلي بعيداً عن منطقة الخياطة ليبقى حر الحركة.

Illustration 8

6. اثقب فتحتين في الطرف العلوي من وجه الحزام.

Illustration 9

7.  استخدم البرشام لتثبيت الشريحة الداعمة مع الحزام من خلال الثقوب.




8.  قم بإدخال الحزام عبر فتحات المشبك حتى يصل الى الشريحة الداعمة، مع الأخذ بالحسبان أن تكون المنطقة المفتوحة الواسعة من المشبك باتجاه طرف الحزام كما هو موضح.



9. قم بإدخال الحزام الداخلي عبر فتحة العصا. بعد ذلك أدخل الأحزمة عبر فتحة الشريحة الداعمة.



10. اسحب العصا باتجاه المشبك لكي تحافظ على طول إضافي من الحزام الداخلي في هذه المنطقة حيث انها ضرورية في عملية الشد.

11. .قم بتمرير الأطراف العلوية للحزام من خلال فتحة الابزيم الخالية من الأسنان، ثم قم بثنيها نحو الأعلى وأعد تخييطها بالحزام نفسه. كرر عملية الخياطة أكثر من مرة.



12. قم بإزالة أي خيوط زائدة.

13. قص طرف الحزام بشكل بيضاوي. قم بكي طرف الحزام ليسهل إدخاله عبر الإبزيم.



14. قم بخياطة شريط اللصق الذاتي (فلكرو) الأبيض الخشن في منتصف الشريط الناعم لتشكل
حزام المشبك. مع العلم أنه يتم تدوين وقت البدء باستخدام حزام وقف النزيف على هذا الشريط.



15. قم بتثبيت حزام المشبك على المشبك باستخدام غراء قوي.



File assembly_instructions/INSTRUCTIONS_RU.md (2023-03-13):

# Список материалов
* Черная лента-липучка шириной 3,5-3,85 см для лицевой стороны ремня, состоит из жесткой (hook)  и мягкой (loop) частей.
* Белая лента-липучка шириной 2 см для клипсы: жесткая и мягкая части.
* Хлопко-полиэстровая тесьма шириной 3,5-3,85 см и толщиной примерно 1,5 мм для тыльной стороны ремня.
* Прочная нерастяжимая нейлоновая тесьма шириной 2,5 см и толщиной примерно 1,3 мм для внутреннего ремня.
* Двухсторонние заклепки с головкой 7 мм.
* Полиэстровая нитка толщиной 0,75 мм для сшивания деталей пояса.
* Клей для фиксации ленты-липучки на клипсе. Цианоакрилатный клей (Суперклей) для напечатанных ABS-пластиком деталей или двухкомпонентная эпоксидная смола для деталей из пластика PETG.
* Напечатанные пластиковые детали.

Black self-adhesive hook and loop tape
White self-adhesive hook and loop tape
Polyester cotton webbing strap
Nylon heavy webbing strap
Double cap rivet
Omni tape

# Инструкция по сбору:
1. Отрежьте ремни необходимой длины, а именно:
  * Черная лента-липучка (жесткая часть: 3 шт. по 6 см и 1 шт. 15 см, мягкая часть: 1 шт. 6 см, 2 шт. 12,5 см каждая, 1 шт. 19 см)
  * Белая лента-липучка (жесткая часть: 1 шт. 20 см, мягкая часть: 1 шт. 20 см)
  * Хлопко-полиэстеровая тесьма (Polyester Cotton Webbing) – 97 см
  * Нерастяжимая нейлоновая тесьма (Nylon Heavy Webbing) – 97 см


Illustration 1

2. Чтобы сформировать лицевую сторону ремня, пришейте подготовленные вами черные ленты (липучки) друг к другу в следующей последовательности: 6 см мягкая часть, 6 см жесткая часть, 12,5 см мягкая часть, 6 см жесткая часть, 12,5 см мягкая часть, 6 см жесткая часть, 19 см мягкая часть, 15 см жесткая часть. Важно, чтобы каждый последующий элемент подкладывался под предыдущий, нахлест должен составить примерно 1 см. Прошейте каждое соединение двумя проходами для увеличения прочности на разрыв. Сделайте второй шов зигзагообразным. Это разровняет место нахлеста и облегчит прохождение ремня через прорезь пряжки.

Illustration 2
Illustration 3

3. Лицевая сторона ремня короче тыльной (хлопково-полиэстеровой тесьмы). Выровняйте лицевую и тыльную сторону так, чтобы на общем конце была мягкая часть черной ленты-липучки длиной 6 см. Сшейте лицевую сторону ремня с тыльной по всей длине с одного бока. Оставьте другой бок открытым, чтобы вставить внутренний ремень. 

Illustration 4

4. Вставьте внутренний ремень между лицевой и тыльной сторонами ремня, а затем сшейте конец внутреннего ремня с наружными ремнями следующим образом:
  * выровняйте концы внутреннего и наружных ремней
  * внутренний ремень должен находиться по центру относительно наружных ремней

Illustration 5

  * прострочите все три ремня (на всю ширину наружных ремней) на расстоянии 3 см от края

Illustration 6

  * прострочите крест-накрест наружные ремни с 3ого до 5ого сантиметра от края.

Illustration 7

5. Закруглите сшитый конец ремня. Сшейте лицевую и тыльную части ремня с другого бока, так чтобы внутренний ремень мог свободно двигаться внутри.

Illustration 8

6. Сделайте два отверстия по бокам с другого края лицевого ремня.

Illustration 9

7. Используя заклепки, закрепите опорную пластину на ремне через сделанные отверстия. Внутренний ремень должен свободно двигаться внутри.




8. С закругленного конца проденьте ремень через отверстия клипсы, пока он не достигнет опорной пластины. Обратите внимание, что клипса должна быть повернута узкой стороной к опорной пластине, как показано на фотографии.



9. Вставьте внутренний ремень через отверстие в ручке ворота. Затем проденьте внутренний и тыльный ремни через прорезь опорной пластины.



10. После установки ручки ворота, ослабьте немного натяжение внутреннего ремня. Так, чтобы можно было сделать пол оборота ручки ворота до того как турникет начнет затягиваться.

Figure 6b

11. Пропустите концы внутреннего и тыльного ремня через беззубчатую прорезь пряжки и пришейте пряжку так, как показано на фотографии. Ремни должны быть сшиты несколькими двойными швами, расстояние от пряжки до опорной пластины должно составить примерно 3 см. Надпись на пряжке должна быть с лицевой стороны ремня.



12. Удалите все лишние нити.

13. Прошейте скругленный конец ремня, чтобы его было легче вставить в пряжку.



14. Застегните белую ленту-липучку сдвинув жесткую часть относительно мягкой примерно на половину длины. Сшейте жесткую и мягкую половинки на конце жесткой части ленты.



15. Приклейте суперклеем мягкую часть ленты-липучки к клипсе. Жесткая лента должна остаться свободной, чтобы ею можно было обернуть клипсу сверху и написать время наложения турникета. 



Обратите внимание: если есть такая возможность, то вместо того, чтобы сшивать лицевую сторону ремня из жестких и мягких отрезков обычной ленты-липучки, можно применить один цельный отрезок ленты типа omni tape. Лента типа omni tape прилипает сама к себе, потому что она сразу сочетает в себе элементы жесткой и мягкой частей на одной и той же стороне (именно на одной стороне, а не мягкая часть с одной стороны, а жесткая с другой).

Чтобы было проще сшивать части ленты-липучки, можно использовать малярный скотч: наклейте все части ленты-липучки на скотч, сшейте части, а затем отклейте скотч.

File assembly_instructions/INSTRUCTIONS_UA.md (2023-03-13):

# Список матеріалів
* Чорна стрічка-липучка шириною 3,5-3,85 см для лицьової сторони ременя, складається із жорсткої (hook) і м'якої (loop) частин.
* Біла стрічка-липучка шириною 2 см для кліпси, жорстка і м'яка частини.
* Бавовняно-поліестерова тасьма шириною 3,5-3,85 см і товщиною приблизно 1,5 мм для тильної сторони ременя.
* Міцна нерозтяжна нейлонова тасьма шириною 2,5 см і товщиною приблизно 1,3 мм для внутрішнього ременя.
* Двосторонні заклепки з головкою 7 мм.
* Поліестрова нитка товщиною 0,75 мм для зшивання деталей пояса.
* Клей щоб прикріпити стрічку-липучку до кліпси. Ціаноакрилатний клей (Суперклей) для деталей, надрукованих ABS-пластиком, або двокомпонентна епоксидна смола для деталей із пластику PETG.
* Надруковані пластикові деталі.

Black self-adhesive hook and loop tape
White self-adhesive hook and loop tape
Polyester cotton webbing strap
Nylon heavy webbing strap
Double cap rivet
Omni tape

# інструкція по складанню:
1. Відріжте ремені необхідної довжини, а саме:
 * Чорна стрічка-липучка (жорстка стрічка: 3 шт. по 6 см і 1 шт. 15 см, м'яка стрічка: 1 шт. 6 см, 2 шт. 12,5 см кожна, 1 шт. 19 см)
 * Біла стрічка-липучка (жорстка стрічка: 1 шт. 20 см, м'яка стрічка: 1 шт. 20 см)
 * Бавовняно-поліестерова тасьма (Polyester Cotton Webbing) - 97 см
 * Нерозтяжна нейлонова тасьма (Nylon Heavy Webbing) - 97 см


Illustration 1

2. Щоб сформувати лицьову сторону ременя, пришийте підготовлені вами чорні стрічки (липучки) один до одного в наступній послідовності: 6 см м'яка стрічка, 6 см жорстка стрічка, 12,5 см м'яка стрічка, 6 см жорстка стрічка, 12,5 см м'яка стрічка, 6 см жорстка стрічка, 19 см м'яка стрічка, 15 см жорстка стрічка. Важливо щоб кожен наступний елемент підкладався під попередній, перекриття елементів повинно становити приблизно 1 см. Прошийте кожне сполучення двома проходами для збільшення міцності на розрив. Зробіть другий шов зигзагоподібним. Це розрівняє місце перекриття і полегшить проходження ременя через отвір в пряжці.

Illustration 2
Illustration 3

3. Лицьова сторона ременя коротша за тильну (бавовняно-поліестерова тасьма). Вирівняйте лицьову і тильну сторону так, щоб на спільному кінці ременя була м'яка стрічка довжиною 6 см. Зшийте лицьову сторону ременя з тильною по всій довжині з одного боку. Залиште інший бік відкритим, щоб вставити внутрішній ремінь. 

Illustration 4

4. Вставте внутрішній ремінь між лицьовим та тильним, а потім зшийте кінець внутрішнього ременя з зовнішніми ременями наступним чином:
  * Вирівняйте кінці внутрішнього та зовнішніх ременів
  * Внутрішній ремінь має знаходитись по центру відносно зовнішніх ременів

Illustration 5

  * Прострочить всі три ремені (на всю ширину зовнішніх ременів) на відстані 3 см від краю

Illustration 6

  * Прострочить навхрест зовнішні ремені з 3ого до 5ого сантиметру від краю

Illustration 7

5. Закруглить зшитий кінець ременя. Зшийте лицьову частину ременя із тильною з іншого боку, так щоб внутрішній ремінь міг вільно рухатися всередині.

Illustration 8

6. Виконайте два отвори по краях з іншої сторони лицьового ременя.

Illustration 9

7. Використовуючи заклепки, закріпіть опорну пластину на ремені через зроблені отвори. Внутрішній ремінь має вільно рухатися всередині




8. З заокругленого кінця протягніть ремінь через отвори кліпси, поки він не досягне опорної пластини. Зауважте, що кліпса має бути повернута вузькою стороною до опорної пластини, як зображено на фотографії.



9. Вставте внутрішній ремінь через отвір в ручці ворота. Потім Протягніть внутрішній і тильний ремені через проріз опорної  пластини.



10. Після встановлення ручки ворота, послабте трохи натяг внутрішнього ременя. Так, щоб можна було зробити пів оберту ручки ворота до того, як турнікет почне затягуватися.

Figure 6b

11. Пропустіть кінці внутрішнього і тильного ременів через беззубчастий отвір пряжки та пришийте пряжку так, як зображено на фотографії. Ремені мають бути зшиті кількома подвійними швами, відстань від пряжки до опорної пластини має скласти приблизно 3 см. Напис на пряжці має бути з лицьової сторони ременя.



12. Видаліть усі зайві нитки.

13. Прошийте заокруглений кінець ременя, щоб його було легко вставити в пряжку.



14. Застебніть білу стрічку-липучку зсунувши жорстку стрічку відносно м'якої приблизно на половину довжини. Зшийте жорстку і м'яку половинки на кінці жорсткої стрічки.



15. Приклейте суперклеєм м'яку стрічку до кліпси. жорстка стрічка має залишитись вільною, щоб нею можна було огорнути кліпсу зверху і написати на ній час накладання турнікету.



Зверніть увагу:  якщо є така можливість, то замість того щоб зшивати лицьову сторону ременя з жорстких і м'яких відрізків звичайної стрічки-липучки, можна застосувати один цільний відрізок стрічки типу omni tape. Стрічка типу omni tape прилипає сама до себе, тому що вона одразу поєднує в собі елементи жорсткої та м'якої стрічок на одній і тій самій стороні (саме на одній стороні, а не м'яка частина з однієї сторони, а жорстка з іншої).

Щоб було простіше зшивати частини стрічки-липучки, можна скористатись малярським скотчем: наклейте всі частини стрічки-липучки на скотч, зшийте частини, а потім відклейте скотч.

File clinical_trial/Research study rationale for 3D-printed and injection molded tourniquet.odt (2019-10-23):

No one should bleed to death. This is the main goal of Gaza's stop-bleeding campaign. The production of 3D-printed and injection-molded tourniquets in Gaza will ensure that tourniquets are available to all providers when needed, regardless of the blockade or other political factors.

This research study seeks to confirm with research that the tourniquets used in Gaza for the past two years are at least equal in efficacy to premium brand tourniquets, including the Combat Application Tourniquet (CAT) commonly used by military forces around the world.

# Defining the problem

Uncontrolled acute arterial bleeding (e.g., from a femoral artery) can kill a person in less than 5 minutes.‏‏ Most deaths by exsanguination are due to the inability of the injured person or bystanders to provide first aid pending professional assistance.

Traditional methods of bleeding control for life-threatening external bleeding make use of the tourniquet as a last resort rather than the first choice. This can lead to the loss of a a life-threatening or even fatal amount of blood.

The use of simple tools such as tourniquet in the first seconds of acute bleeding from limb injuries has been shown to have a six-fold reduction in exsanguination-related mortality as well as significant decreases in exsanguination-related morbidity. This is confirmed by several studies and the practical experience of military doctors treating wounded soldiers on the battlefield.

These studies also demonstrated that concerns about the medical complications of the tourniquet application are unfounded, as affected limbs can withstand complete cessation of blood perfusion for two hours without complications. This is confirmed by the use of tourniquets by orthopedic and plastic surgeons to stop limb perfusion intraoperatively without significant complications. This time is more than enough to transport the patient to the nearest specialized hospital under normal conditions.

# International experiences

In 2015, widespread mass shootings and bombings in the United States and elsewhere led to the launch of the first national stop bleeding campaign in the United States. This initiative aimed at training the community to deal with life-threatening bleeding.

The American College of Surgeons (ACS) adopted the task of preparing the national campaign's training program. This program relies on the use of auxiliary tools to stop bleeding quickly and effectively, such as tourniquets and quick clot gauze.

The ACS adopted the Combat Application Tourniquet (CAT) as a key tool to stopping life-threatening bleeding from the limbs because of its ease and speed of use. The CAT is certified and licensed by the U.S. Food and Drug Administration (FDA) as a medical device.

# Application in Gaza

After learning from the American experience, medical authorities in Gaza realized the importance of transferring this experience to the local context. A joint governmental-academic venture started training the local community on how to deal with massive external bleeding, especially as this community is exposed to regular attacks from Israeli forces. Some of these attacks use weapons that lead to serious injuries, especially In the limbs, that require rapid interventions to stop life-threatening bleeding.

Some emergency medicine and disaster experts in Gaza wanted to establish a similar program and launch a national campaign or initiative to train the provider and lay communities in techniques to stop deadly bleeding in quick and effective ways. The team tried to import the CAT from abroad, but Israeli authorities refused to permit entry of the devices into Gaza. This led the team to make all efforts to produce tourniquets locally to bypass this challenge.

Experts in medicine and engineering were consulted about producing and manufacturing a tourniquet that functions as well as the CAT using locally available resources. Using 3D printing and other manufacturing techniques, a usable prototype tourniquet was created.

# Great March of Return 2018

With the start of the Great March of Return in 2018, health care providers observed the targeting of protesters in the lower and upper extremities by Israeli soldiers, which often led to severe and life-threatening bleeding. This made more urgent the need to train ambulance crews and volunteers to stop exsanguination and bleeding-related mortality and morbidity in an effective way.

Paramedics and first responders resorted to rudimentary methods using available resources to make improvised tourniquets. Unfortunately, these improvised tourniquets are not always effective. This forced the accelerated development and production of 3D printed tourniquets.

The engineering team managed to produce tourniquets for field use and conducted tests on quality, strength and durability of the tourniquet's components. Parts that failed were redesigned to avoid observed weaknesses in the previous versions.

# Training and testing on trainees and volunteers

Groups of medics and volunteers who are involved in field rescues of injured victims in the GMR were trained on how to stop life-threatening bleeding in different ways, the most important of which is the use of the 3D printed tourniquets.

During the training, we tested the ability of 3D printed tourniquets to stop the circulation, confirmed by using a pulse oximeter to check the blood oxygen concentration in the distal limb before and after the placement of 3D printed tourniquets, which proved the ability of the tool to completely stop the perfusion in the tested limb.

# Literature supporting tourniquet use

Studies and research emphasize the importance of using tourniquets as an essential option to stop life-threatening bleeding:

1. http://www.combattourniquet.com/
- Since its combat introduction by the U.S. Army in 2005, the Combat Application Tourniquet® (CAT)– a true one-handed tourniquet – has decreased the mortality rate due to extreme exsanguination by 85%. The U.S. Army Institute of Research deemed it to be 100% effective.
2. https://www.bleedingcontrol.org
- BleedingControl.org is an initiative of the American College of Surgeons and the Hartford Consensus and contains diagrams, news, videos, and other resources contributed by a variety of other private and nonprofit partners to help prepare you in the event you are witness to one of these unspeakable events
- Massive bleeding from any cause, but particularly from an active shooter or explosive event where a response is delayed can result in death. Similar to how the general public learns and performs CPR, the public must learn proper bleeding control techniques, including how to use their hands, dressings, and tourniquets. Victims can quickly die from uncontrolled bleeding, within five to 10 minutes.
3. Military history of increasing survival: The U.S. military experience with tourniquets and hemostatic dressings in the Afghanistan and Iraq conflicts (https://www.bleedingcontrol.org/-/media/bleedingcontrol/files/compendiummilitaryhistory.ashx?la=en)
- The resurgence of tourniquet use in the U.S. military that originated from the Tactical Combat Casualty Care program is discussed as are the specific events that contributed to the expanded use of tourniquets in the military. Statistics regarding the decrease in preventable battlefield deaths in the from extremity hemorrhage are presented. The use of hemostatic dressings in the military is reviewed.
4. Hemorrhage control devices: Tourniquets and hemostatic dressings (https://www.bleedingcontrol.org/-/media/bleedingcontrol/files/compendiumhemorrhagecontrol.ashx?la=en)
- This article draws from the military’s experience with tourniquet use to describe what type of trauma victims are appropriate for tourniquet use in a civilian setting. Teaching points about tourniquets are presented as are common mistakes regarding their use. The role of the Committee on Tactical Combat Casualty Care in recommending tourniquets and hemostatic dressings is reviewed.
5. https://www.journalacs.org/article/S1072-7515(18)30101-7/abstract
- Civilian Prehospital Tourniquet Use Is Associated with Improved Survival in Patients with Peripheral Vascular Injury (http://www.journalacs.org/article/S1072-7515(18)30101-7/abstract) —published as an article in press by the Journal of the American College of Surgeons.
- Tourniquet use has been proven to reduce mortality on the battlefield. Although empirically transitioned to the civilian environment, data substantiating survival benefit attributable to civilian tourniquet use is lacking. We hypothesized that civilian prehospital tourniquet use is associated with reduced mortality in patients with peripheral vascular injuries.

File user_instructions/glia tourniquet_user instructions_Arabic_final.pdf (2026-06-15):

# مازح فقو فيزنلا - ايلغ - تاميلعت مادختسا

ةوطخلا ةيناثلا; بحسا مازحلا ماكحاب دعأو هقاصلإ ىلع هسفن لوح فرطلا .;  ررمت مازحلا نيب يفرط كبشملا يف هذه ةوطخلا .; ررم مازحلا نيب يفرط كبشملا قوفو اصعلا .; هن طيب تقولا ضيبا .; ررم طي تقولا ضيبا قوف; هقصلا فرطب; ّ مازحلا مث; كبشملا رخا .; ةوطخلا ةسماخلا; Tourniquet: Model 007 54 Craig Street London ON N6C 1E8; ةوطخلا ىلوا; عض مازح فقو فيزنلا لوح فرطلا ىلع ةفاسم ٧.٥ مس قوف ةقطنم فيزنلا .; عض مازحلا ىلع دلجلا ةابم ول تعطتسا .; ريضحت مازح فقو فيزنلا; ول مل نكي زهاج , ررم فرط مازحلا نم لخ; ةوطخلاب ىلوا; تبث اصعلا ىدحإب يفرط كبشملا تبثيل هناكم .; ةوطخلا ةثلاثلا ةوظخلا ةعبارلا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

قوت ّع نأ مازحلا زهاج لعفلاب نأب نوكي مازحلا لخاد ميزبإ مازحلا ( ةلكبلا ) امك يف ةروصلا

فيوجت ميزبإ مازحلا ( ةلكبلا .) مث ّ أدبإ

لمعتسا مازح فقو فيزن رخآ ّ | ةيقابلا ( ةوطخ ٤ & ٥ ) مث


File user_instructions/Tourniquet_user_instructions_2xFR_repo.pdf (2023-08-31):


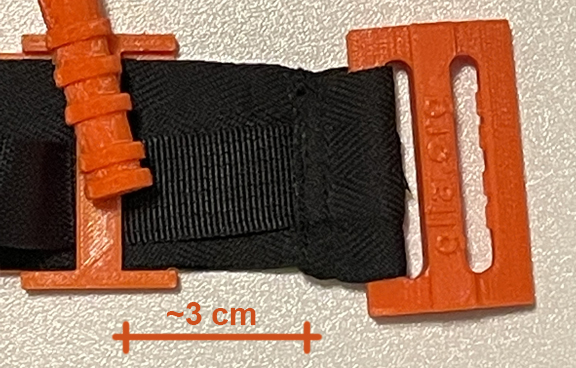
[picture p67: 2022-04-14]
assets/instructions/figure7b.jpg

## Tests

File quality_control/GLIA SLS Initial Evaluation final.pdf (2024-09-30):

| SLS testing Initial Evaluation GLIA
Revision: A | | Page 1

### 1. Summary

1.1. This report is a summary of various initial evaluations performed in order to determine the feasibility of SLS (selective laser sintering) parts in the manufacturing of the Glia tourniquet. Initial evaluation shows SLS has several disadvantages and limitations that make it impractical for producing parts such as those used in the Glia tourniquet.

### 2. Purpose

2.1. The report is composed of early testing that does not comprehensively evaluate the material or manufacturing process. This report should not be considered a validation and should be used to inform decisions related to further testing and formal validation. Testing was carried out across multiple institutions using different test methods, tools and data. Some results are de-identified and should be considered anecdotal.

### 3. Scope

3.1. Testing was performed across multiple institutions and locations with different sample sizes, test methods and reporting methods. This report details the overall evaluation actions and results.

### 4. Test participants

4.1. OpenWorks- A community maker space located in Baltimore MD (https://www.openworksbmore.org/)
4.2. FormLabs
4.3. Unnamed medical research institution
4.4. Baltimore, Maryland fire department

### 5. Testing Results

5.1. Open Works
5.1.1. OpenWorks assembled thirty-eight Glia tourniquets approximately 25 MAY 2022. The SLS components were made using FormLabs PA12

| SLS testing Initial Evaluation GLIA
Revision: A | | Page 2

nylon powder on a Fuses 1 printer. Upon review of images sent from OpenWorks several deviations in the work instructions were identified.

5.1.1.1. Counter to the work instructions the inner belt is exposed due to feeding the inner and outer belt assembly down through the buckle instead of up.
5.1.1.2. Cross stitch at the start of the belt is missing.
5.1.1.3. Time piece velcro is black instead of white
5.1.1.4. Two-sided rivets are missing
5.1.2. OpenWorks tourniquets were tested using the University of Western Ontario tourniquet tester [1]. The tourniquet did not break or deform and provided similar readings to FDM tourniquets produced at Glia.
5.2. Unnamed Medical Research Institution
5.2.1. Unknown number of tourniquets were assessed using a “trauma dummy” of unknown make and model and by application to a living subject and verifying full occlusion using a pulse oximeter. Both test cases resulted in acceptable performance according to the evaluator.
5.3. FormLabs
5.3.1. Testing was performed on an unknown number of units produced by OpenWorks. These units were affected by the same deviations as outlined in section 5.1.1. A tensile test machine was used to evaluate the overall tensile strength of the assembled units. (PASCO Scientific ME-8236).
5.3.2. Failure occurred at 800N (fig 1.) where the buckle and backplate broke. (fig 2, fig 3.)

| SLS testing Initial Evaluation GLIA
Revision: A | | Page 3

Fig 1.

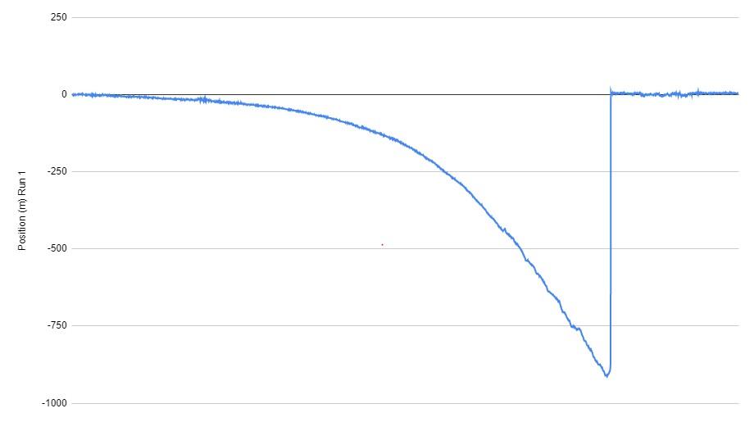
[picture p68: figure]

Fig 2. | Fig 3.

| SLS testing Initial Evaluation GLIA
Revision: A | | Page 4

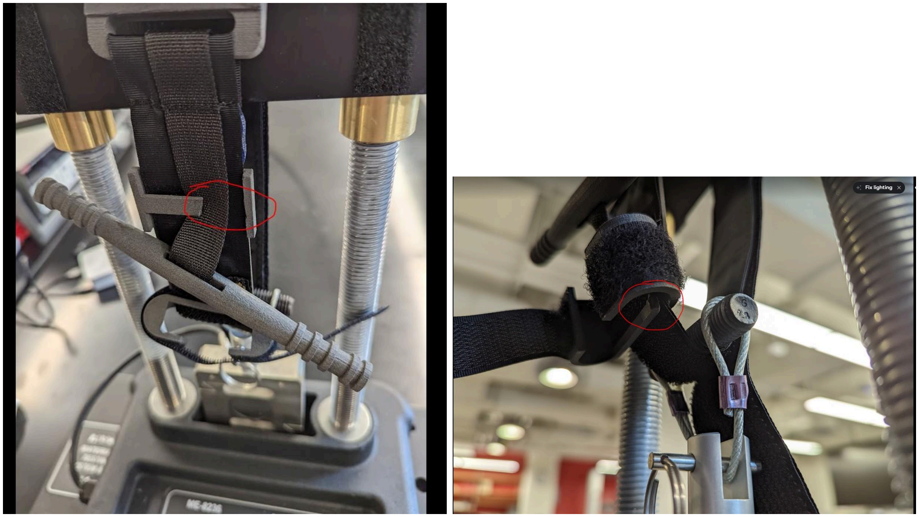
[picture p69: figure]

### 6. Results

6.1. SLS has several limitations that make use in the Glia tourniquet impractical. Rapid prototyping is a constantly changing field and further evaluation should be considered as methods and technologies evolve. This initial evaluation should be used as a starting point when considering using SLS as a production method.
6.1.1. Cost- SLS machines are significantly more expensive than FDM [2]. Rapid prototyping as a production method for devices such as the Glia tourniquet are generally selected due to lack of capital or infrastructure needed for more traditional methods such as injection molding. The cost of SLS printers is realistically unachievable for community level production organizations.
6.1.2. Material characteristics- Nylon SLS has been considered to be generally more durable and stronger than ABS parts produced using FDM. However studies have shown FDM is stronger [2]. Nylon as a material has higher tensile strength, durability and UV resistance compared to ABS but is susceptible to moisture absorption and may not benefit from the tensile advantages due to the manufacturing process of SLS. Due to the high probability of tourniquets being transported and used in diverse outdoors environments, incorporating a raw material that absorbs

| SLS testing Initial Evaluation GLIA
Revision: A | | Page 5

moisture and thus affects downstream clinical operation would be ill-advised.

### 7. References

7.1. [1] Liu, Dawei, et al. "Distributed manufacturing of an open-source tourniquet testing system." HardwareX (2023): e00442.
7.2. [2] SOFU, Mehmet Mahir, et al. "Comparison of Strength, Surface Quality and Cost of Different Additive Manufacturing Methods." İmalat Teknolojileri ve Uygulamaları 4.1: 25-36.

### 8. Definitions

8.1. SLS- Selective Laser Sintering
8.2. FDM- Fused Deposition Modeling

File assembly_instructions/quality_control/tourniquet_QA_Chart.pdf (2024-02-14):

1. End without buckle must be rounded, and sewn closed with no fraying edge.
2. Box stitch (square with an x) must be 30mm from the rounded end.
3. Stitching down both sides of the strap, and holding the Hook and Loop pieces together, must not have any gaps or openings.
4. Clip must be on the strap with the caps pointing toward the windlass.
5. The inner strap must move freely and not be pinched by rivets or stitches.
6. Rivets must be totally secure under pressure, with no wiggle.
7. Windlass must be located between the rivets and the bridge of the backplate.
8. Slack on inner strap must be 25mm.
9. Distance from bridge of backplate to stitching at buckle must be 35mm.
10. Both inner and outer straps are sewn through the buckle, and the slot on the buckle that is empty has teeth and is facing the end of the tourniquet.

## GLIA TOURNIQUET QUALITY ASSURANCE CHART

clip
cap

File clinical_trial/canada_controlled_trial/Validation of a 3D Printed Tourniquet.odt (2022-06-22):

Validation of a 3D Printed Tourniquet For Hemorrhage Control in a Controlled Setting

Background

Application of a limb tourniquet is vitally important in temporizing life threatening hemorrhage following trauma in hospital and pre-hospital settings¹. Currently there are no standardized testing protocols to determine the efficacy of tourniquet designs in civilian literature. In 2019, the Committee on Tactical Combat Casualty Care (CoTCCC), an arm of the U.S. Department of Defence, published a review paper on tourniquet design, including a 50-point rating scale based with both subjective and objective measures of performance including arterial occlusion scoring, speed of application, ease of use, pressure scoring and safety metrics². This scoring system is focused on making recommendations on tourniquet designs for the U.S. Military. Throughout the years, many head-to-head tourniquet studies have been performed in controlled environments, focusing on performance metrics around arterial occlusion³⁻⁸.

Despite little innovation in design in recent decades, tourniquets can be both expensive and unobtainable during times of humanitarian crisis. Recent advancements and mass dissemination of 3D printing technologies may be able to fill this gap if these devices can create reliable and safe products. In this study we will compare the efficacy of a 3D printed tourniquet with a standard CAT Gen 7 tourniquet, focusing on performance of each device in a controlled setting.

Methods

In this trial we will as recruit EMS personnel with previous training in tourniquet application to deploy both a 3D printed tourniquet and a control CAT tourniquet to a volunteer subject’s thigh. The order of application (3D printed vs CAT) will be pre-randomized prior to application. A doppler ultrasound probe will be used to determine loss of popliteal pulse. Volunteers and subjects will be privy to doppler waveforms and feedback sounds throughout the trial to act as a surrogate for hemorrhage. EMS volunteers will then participate as the subject for the next volunteer.

Inclusion criteria will include volunteer EMS providers with prior training on tourniquet application. Exclusion criteria will include previously known vascular disease, previous lower limb surgery, previous or active DVT, ongoing infection to a limb, or open wound.

The primary outcome will be percentage of trials with successful arterial occlusion. Secondary outcomes will include time to arterial occlusion, incidence of trial failure due to mechanical failure of the tourniquet and intolerance of the procedure by the subject as the reason for trial failure. Successful arterial occlusion will be defined as 1) successful occlusion of the popliteal artery as detected by doppler ultrasound, 2) windlass mechanism locked into plastic gate and 3) arterial flow resumed at tourniquet release.

Discussion

We hypothesize that the 3D printed tourniquet is non-inferior to the CAT Gen 7 tourniquet in controlled settings. Unfortunately, placing a tourniquet in the lab is not the same as placing it in the field as situational stress can cause failure such as overtightening and damaging the tourniquet. This is discussed frequently in CoTCCC affiliated publications (ex. In ‘care under fire’ scenarios) and is likely true for EMS providers as well. We therefore hope that this controlled study will serve as the basis for more involved civilian EMS studies in the real world. Future planned studies may involve a randomized control trial of 3D printed vs standard issued tourniquets deployed by EMS colleagues in real world trauma. There are also opportunities to further develop tourniquet testing protocols to decide which designs are appropriate for pre-hospital systems .

References

1. Walters TJ, Wenke JC, Kauvar DS, McManus JG, Holcomb JB, Baer DG. Effectiveness of self-applied tourniquets in human volunteers. Prehosp Emerg Care. 2005 Dec;9(4):416–422. PMID: 16263675

2. Montgomery HR, Hammesfahr R, Fisher AD, Cain JS, Greydanus DJ, Butler FK, Goolsby C, Eastman AL. 2019 Recommended Limb Tourniquets in Tactical Combat Casualty Care. J Spec Oper Med Peer Rev J SOF Med Prof. 2019;19(4):27–50. PMID: 31910470

3. Savage E, Pannell D, Payne E, O’Leary T, Tien H. Re-Evaluating the Field Tourniquet for the Canadian Forces. Mil Med. 2013 Jun 1;178(6):669–675.

4. Kragh JF, Moore VK, Aden JK, Parsons DL, Dubick MA. Short Report Comparing Generation 6 Versus Prototype Generation 7 Combat Application Tourniquet® in a Manikin Hemorrhage Model. J Spec Oper Med Peer Rev J SOF Med Prof. 2016;16(1):14–17. PMID: 27045489

5. Gibson R, Housler GJ, Rush SC, Aden JK, Kragh JF, Dubick MA. Preliminary Comparison of New and Established Tactical Tourniquets in a Manikin Hemorrhage Model. J Spec Oper Med Peer Rev J SOF Med Prof. 2016;16(1):29–35. PMID: 27045491

6. Heldenberg E, Aharony S, Wolf T, Vishne T. Evaluating new types of tourniquets by the Israeli Naval special warfare unit. Disaster Mil Med. 2015;1:1. PMCID: PMC5327874

7. Kragh JF, Newton NJ, Tan AR, Aden JK, Dubick MA. New and Established Models of Limb Tourniquet Compared in Simulated First Aid. J Spec Oper Med Peer Rev J SOF Med Prof. 2018 Summer;18(2):36–41. PMID: 29889953

8. Glick CY, Furer MA, Glassberg CE, Sharon R, Ankory MR. Comparison of Two Tourniquets on a Mid-Thigh Model: The Israeli Silicone Stretch and Wrap Tourniquet vs. The Combat Application Tourniquet. Mil Med. 2018 Mar 1;183(suppl_1):157–161.

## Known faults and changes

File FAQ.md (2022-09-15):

# Frequently Asked Questions

Our team at Glia receives many inquiries from additive manufacturers wanting to produce tourniquets around the world, most recently in Ukraine. We thank everyone for their desire to help create quality devices. These are the most frequently asked questions, which we will be updating as the project progresses.

**1. Are there any patent restrictions on the Glia tourniquet?**

*There are no patent infringements in our design to the best of our analysis and knowledge. However, if the design is modified from Glia's current source files, this becomes a possibility.*

**2. Can I use my print farm to send plastic parts to Glia?**

*No. At this time Glia does not need decentralized manufacturing of plastic parts of tourniquets.*

**3. I do not want to print in ABS or PETG. Can I use a different filament?**

*No. To date, mechanical testing has only been done on ABS and PETG. Other filaments such as nylon are currently undergoing testing, and we will post the results of those tests to this repository.*

**4. Sewing and assembling the tourniquet is very labor intensive. Do you have detailed instructions for that?**

*We created a more detailed sewing assembly guide with feedback and review from professional sewing experts. The guide can be found in this repository, and is linked from the README file.*

**5. How do I send tourniquets to places in need such as Ukraine, Gaza, Burma, etc.?**

*Glia partners with humanitarian organizations to transport tourniquets to areas in need. If you would like to order tourniquets or sponsor injection molded production, please email info@glia.org.*

**6. I made a tourniquet. How do I test it?**

*No open source standards exist for tourniquet unit testing or production testing. Glia is in the process of documenting clinical parameter standards by partnering with University of Western Ontario (UWO) FAST Research Group, with publication anticipated by end of 2022. The developments of these standards will allow Glia to create production, material, and quality assurance standards.*

**7. I am an engineer who would like to help develop standards for the Glia tourniquet. How can I help?**

*We are grateful for our testing partnership with the University of Western Ontario and other engineering volunteers. If you would like to help us develop standards, particularly for materials specifications, please email info@glia.org.*

**8. My local store does not have the types of velcro and strapping in your assembly guide. Can I use alternate materials?**

*Supply chain gaps and international access volatility to fabric materials create challenges in tourniquet manufacturing. There are also variations in fabric dimension and strength among Canada, US, EU, and other international suppliers. Currently, fabrics that differ from our BOM have not yet been tested. We plan to test alternate materials, specifically for materials in the EU market, and will share those results through this repository and on social media.*

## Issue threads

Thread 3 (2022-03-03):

### ISSUE TITLE
Please add some more instructions for assembly

### ISSUE THREAD

**Issue by sbamueller** [GliaX/tourniquet#3]
Hi,
I'm just trying ti print the tourniquet. What kind of velcro and nylon straps do I need?

**Comment by tareko** [comment]
Hi @sbamueller ! Thank you for this. Indeed one of the deficiencies at the moment is a lack of information on the non-printed parts.

@shakersh : Could you comment on this please?

tarek : )

**Comment by tareko** [comment]
Haven't forgotten about this. I will poke @shakersh again and will address this issue myself in the coming days if he's not able.

tarek : )

**Comment by shakersh** [comment]
@sbamueller Hello and sorry for missing
there is some instruction for made your tourniquet
go to tourniquetmedia repo. you will see the file

**Comment by tareko** [comment]
Thank you so much, @shakersh ! 

@sbamueller : Here are the instructions:

https://github.com/GliaX/tourniquetmedia

**Comment by tareko** [comment]
OK, I've pulled these instructions into the main repo and converted them to markdown. I will close this issue now.

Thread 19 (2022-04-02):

### ISSUE TITLE
Polish translation - step 10 - mistranslated 

### ISSUE THREAD

**Issue by apopanda** [GliaX/tourniquet#19]
Title.
In the polish translation, it says:
Gdy drążek wyciągarki został umieszczony, załóż względem niego pewien luz paska.
which roughly translates to 
"When you insert the windlass, allow some slack in the belt". 
As per talk with mr M. Al-Attar on Mattermost, in this step we should remove the slack, not add more of it / allow some of it.

**Comment by tareko** [comment]
Thank you @apopanda . Could you give a new translation?

**Comment by tareko** [comment]
I see the error and how it was misinterpreted. "take up any slack" was interpreted as "add slack"

**Comment by apopanda** [comment]
Copypasting from mattermost:
The translation: 
Gdy drążek wyciągarki został nawleczony na wewnętrzny pasek, napnij pasek. Wewnętrzny pasek powinien być maksymalnie naprężony.

Translates to when the windlass is put through the inner belt, make it tight. The inner belt should be maximally tight


I also think we might want to consider removing idioms from the english version, like the one I mentioned earlier. Running them through google translate to make sure what they mean sometimes get conflicting results. Simple / idiot proof language would be better in this case I feel

**Comment by tareko** [comment]
That's a great suggestion, @apopanda . I will review for simple english

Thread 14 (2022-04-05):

### ISSUE TITLE
Any particular reason why ABS material?

### ISSUE THREAD

**Issue by arcusfelis** [GliaX/tourniquet#14]
Material question.

PLA or PETG are more common and easier to print. Any particular reason why it should be avoided?

**Comment by xchg-dot-ca** [comment]
PLA is a bit more brittle
PETG probably better choice here also easier to print. Crappy ABS prints with poor layer adhesion will be way worse then PETG or even PLA.
But again there are crappy PETG brands as well. So for such application I would use well tested plastic brand that prints well on your printer.
Carbon fiber filled nylon is probably the best choice ( providing you can print it and find in colors other than black )

**Comment by pierrotsmnrd** [comment]
Hi everyone. Quick questions related to the material : 

1. What are the required properties for the material to print tourniquets ? resistant but not brittle ? slightly flexible ? 
2. Would ASA also be a suitable material ? 
3. I have a left-over spool of Prusa PETG, so I intend on experimenting with this first before buying any other filament. My question is : Has there been 3D printed tourniquets in PETG already produced and successfully used without problem ? 

If so, it's worth I experiment and then produce in PETG (more convenient for me, easier to print), otherwise I'll switch to any other recommended material (ABS, or ASA if suitable as well)

I'm based in Strasbourg, France, and a local Ukrainian association named [PromoUkraina](https://promoukraina.fr/) makes convoy to Ukraine to provide with collected food and medicines. I'm already in touch with them, I know they could also send the tourniquets. I'm very motivated in producing them.

**Comment by BobBaumeisterXL** [comment]
Great Projekt!
Asa and Petg shoud also do Job.
I am not realy sure if an infill of 100% is needed, we will do some tests.
The heatbed temp for abs shoud be an little bit hihger  something around 110 degree.
I also created an version with brimears wich makes it possible to print it much faster.
Feel free to contact me if u need an copy.

**Comment by talentedmrripley** [comment]
This article from a member of the Glia team has some info on the material selection - https://trklou.medium.com/reinventing-3d-printed-tourniquets-for-ukraine-is-a-mistake-be2937f0ad65

**Comment by arcusfelis** [comment]
Good article.

ok, so for back plate should be flexible and don't break (PETG makes sense).

PLA is not ok, because of storage under sun and high temps - which is kinda important for Gaza. Also, in humid conditions. It is good idea to seal produced tourniquets into some kind easy to unpack plastic bag anyway.

Windlass _probably_ could be from PLA, because it would be hard to break anyway - it does not have small elements. But there is no reason just to use PETG anyway.

The other question is about 100% infill. 75% geroid is producing stronger prints (especially visible on the clip). But geroid makes less flexible backplate (which is equal to making it thicker). 

Also, cooling when printing. Use as little cooling when printing as possible (important both for PLA and PETG). Makes a stronger build.

**Comment by tareko** [comment]
Hello friends! Although I've been active with commits the past little while, I have neglected the issues. Notifications are now fully on, so I shouldn't miss more.

TL;DR: **NO PLA**, **YES PETG**, **YES ABS**

Thank you all for the great discussion. As noted above by @arcusfelis , our environment in Gaza required a hearty plastic, and recycled ABS is readily available there. As @xchg-dot-ca noted, badly-printed or low quality ABS is a huge problem. It took us time to get the settings and the quality control (QC) right on these.

We completed structural tests and PETG is a plastic we can now recommend. We'll publish the details in the coming weeks once we properly analyze and write it up. We haven't tested Nylon, ASA, etc., and don't recommend them until we can properly test them.

**Comment by tareko** [comment]
As no action on this for a bit, going to close!

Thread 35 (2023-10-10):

### ISSUE TITLE
Line 70 needs language corrected

### ISSUE THREAD

**Issue by jenwilsonglia** [GliaX/tourniquet#35]
Line 70 needs language corrected from "back plate" to "bridge of back plate"

**Comment by darigovresearch** [comment]
@jenwilsonglia happy to make a pull request to change this if this is still a problem.

What was the file ?

Couldn't find `back plate` on line 70 of any file currently

https://github.com/search?q=repo%3AGliaX%2Ftourniquet+back+plate&type=code

**Comment by jenwilsonglia** [comment]
This issue has been resolved, but we forgot to close it. Thanks for bringing it to our attention.

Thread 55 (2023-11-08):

### ISSUE TITLE
[FEATURE REQUEST] Add source files for user instructions

### ISSUE THREAD

**Issue by darigovresearch** [GliaX/tourniquet#55]
Can see that currently user instructions are in .pdf form, having the source files would make it easier to make other language translations

https://github.com/GliaX/tourniquet/tree/master/user_instructions

**Comment by jenwilsonglia** [comment]
We'll put this on the agenda for the next tourniquet meeting on Oct. 18th

**Comment by darigovresearch** [comment]
Thanks for the update, happy to jump on a call if that helps to discuss this & other items if the timings work

**Comment by jenwilsonglia** [comment]
User instructions are very specific and having them translated by anyone isn't feasible. If anyone wants to have the user instructions translated into a specific language, please create an issue to do so.

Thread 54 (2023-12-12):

### ISSUE TITLE
[FEATURE REQUEST] Add PETG print settings to readme

### ISSUE THREAD

**Issue by darigovresearch** [GliaX/tourniquet#54]
Design intent says PETG is also acceptable, thought it would be able to add the print settings to the readme with the settings you have been using 

Design intent https://github.com/GliaX/tourniquet/blob/master/assembly_instructions/quality_control/design%20intent.md

Print settings https://github.com/GliaX/tourniquet#print-settings

**Comment by jenwilsonglia** [comment]
For Design Intent, we could change first paragraph to "ABS and PETG are acceptable materials to use to print the plastic parts of the tourniquet. PLA is not an acceptable material because it does not withstand exposure to UV light or exposure to the elements well." 

For Print Settings, let's add PETG and distinguish the different bed temps (85 C for PETG). Layer Height and Infill are the same for ABS and PETG.

Let me know if you want to create the pull request, or if you'd like me to do it.  Thanks

**Comment by darigovresearch** [comment]
Thanks @jenwilsonglia for the feedback, pull request https://github.com/GliaX/tourniquet/pull/63 should resolve this issue if merged

**Comment by jenwilsonglia** [comment]
Pull request #63 has been merged. Thanks @darigovresearch !

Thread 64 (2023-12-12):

### ISSUE TITLE
Include quality control folder on the main readme

### ISSUE THREAD

**Issue by apopanda** [GliaX/tourniquet#64]
https://github.com/GliaX/tourniquet/tree/master/assembly_instructions/quality_control folder contains very useful things, but we aren't linking to it from the main readme. We should add a heading and link to it explaining the files

**Comment by darigovresearch** [comment]
Thanks for raising the issue @apopanda, do you want to make another pull request for this?

**Comment by apopanda** [comment]
@darigovresearch sorry, no time at the moment, I'm full in device production mode right now

**Comment by jenwilsonglia** [comment]
@darigovresearch I've linked the QA folder in the Readme file.

**Comment by jenwilsonglia** [comment]
I'm going to close this out, but let me know if there is an issue with the link.

**Comment by apopanda** [comment]
Need to add it to the polish translation later

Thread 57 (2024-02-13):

### ISSUE TITLE
[FEATURE REQUEST] Source files for images with text

### ISSUE THREAD

**Issue by darigovresearch** [GliaX/tourniquet#57]
Thought it may be helpful to have the source files of images to help with making updates if the design changes but also in particular for any text in images that will require changes in the text for translations

Example of French assembly instructions but with English text in the images

Alternative is to have any text to be outside of the image so images don't need to be translated

**Comment by jenwilsonglia** [comment]
Still working on this...

**Comment by jenwilsonglia** [comment]
All raw photos for assembly instructions that had text, have now been uploaded into the assets folder with no text.

**Comment by darigovresearch** [comment]
Thanks for the updates and for the raw files. What software do you use to make the images with the text?

**Comment by jenwilsonglia** [comment]
Hi George,

I used Gimp to make the images with the text.

-Jen

March 2, 2024 10:04 AM, "Darigov Research" ***@***.*** ***@***.******@***.***>)> wrote:
	Thanks for the updates and for the raw files. What software do you use to make the images with the text?

**Comment by jenwilsonglia** [comment]
I used Gimp to make the images with text.

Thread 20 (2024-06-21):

### ISSUE TITLE
questions regarding webbing materials

### ISSUE THREAD

**Issue by DenysGonchar** [GliaX/tourniquet#20]
I'm looking for the recommended webbing materials at the Polish/European stores, and experience some difficulties. That would be nice to understand what are the possible alternatives.
Also some information is missing in [assembly_instructions](../blob/master/assembly_instructions/INSTRUCTIONS_EN.md)

please answer these questions:

- It's hard to find 3,85 cm wide webbing/velcro strap (3,85cm velcro is not available at all), and it's hard to work with 3,5 cm strap. So please clarify if any of the following alternatives is fine:
  - 4 cm is a very common and easy to find width. But taking into account that width was explicitly reduced in this [commit](https://github.com/GliaX/tourniquet/commit/dd9fa25da8adfd86979d8be48006c96247e79232), I assume that 4cm is not a recommended option for the current design of the plastic parts. But if 4cm is a bit too wide, can we just extend the holes a little in the plastic parts (and probably increase the size of parts as well) instead of narrowing the width of the belt?
  - 3,5 cm wide webbing is less common than 4cm, but it's possible to find. However, it's harder to sew the belt. Can we take a bit narrower internal belt in this case, e.g. 2cm wide instead of 2,5
- A polyester-cotton webbing strap for the back face of the belt is not common, usually it's either synthetic or cotton. From my understanding, pure cotton is a better option as there can be a direct contact with the skin. Also, it doesn't look like we put too much tension on the back face belt while tightening the tourniquet, so reinforcement with polyester is not necessary. Please clarify if 100% cotton strap is fine for the back face of the belt.
- There is no information about the required thickness of the back face of the belt. From my understanding, it must distribute the pressure generated by the internal belt. But from another point, if it's too thick, it can cause issues during application (e.g. it can be hard to fit in into the buckle). It seems that 2-2,5 mm is an optimal thickness, but it's just my impression and I don't have any real field experience. There are many options available in the market, from 1mm to 4mm thick, so please provide some recommendation.
- I cannot find nylon webbing strap for internal belt, more over there are no webbing straps made of nylon in the local market. But there are 2 other options that are widely available: polyester and polypropylene. Both materials are stretching less than nylon, which is better in our case. 
  - according to the various sources available for analysis, polyester shows even better abrasion and UV resistance than nylon
  - polypropylene is less strong/resistant, from another perspective it's also widely available, and it's also used in heavy-duty applications. I'm not sure how critical UV resistance is, since the strap is mostly covered from all sides. And also we are going to tight it just once or a maybe few times. So maybe it's a "good enough" option.

And in the end, it is very important to have some well-defined QA procedures. It's required for mass production, checking prototypes and testing if something is changing (e.g. usage of alternative materials, minor optimizations in sewing, etc.)

Please, provide your comments and extend assembly instructions. I can help with Ukrainian, Polish and Russian translations.

**Comment by apopanda** [comment]
Note: none of what I'm saying comes from @tareko or Glia, I'm just another maker that made some units already, around your area.

The 40mm velcro you mention will be 3.85 if you measure it. Most of the "40mm" velcro is actually 1.5 inch, which is 3.8. As for the webbing, you can find it for example here: https://allegro.pl/oferta/tasma-nosna-bawelniano-poliestrowa-38mm-1m-11809897469 - I see that you're based in Cracow, so I hope allegro links work for you. I wouldn't go to 3.5cm webbing and internal belt - the STLs are made for the "40mm" which is actually a 1.5 inch. 

As for the nylon - try 'poliamide' - more hits that way. No idea if there's much difference, for sure it's closer than polyester is.

As for the QA procedures - yeah, it's a problem Glia is trying to solve. They're working on getting the documentation to be more precise, and the testing is on the horizon, but it's still some time away. There are independent groups trying to figure it out in the meantime, nothing concrete yet though.

**Comment by jenwilsonglia** [comment]
Closing this issue as the outer strap info has been changed/specified on the updated BOM.

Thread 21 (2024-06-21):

### ISSUE TITLE
Review english documentation for Simple English

### ISSUE THREAD

**Issue by tareko** [GliaX/tourniquet#21]
Review English Language documentation to reduce chances of translation errors.

First raised by @apopanda in Issue #19

**Comment by apopanda** [comment]
I'll raise the step 10 issue too. Today at the meeting we opted for adding 2.5cm of slack to the windlass rod. This needs to be specified instead of the "remove all slack" we have there right now.

**Comment by jenwilsonglia** [comment]
Closing this issue due to updated comprehensive assembly instructions in simple English.

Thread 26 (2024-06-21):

### ISSUE TITLE
material testing results

### ISSUE THREAD

**Issue by alexgubanow** [GliaX/tourniquet#26]
hi, we are testing some materials for stretching against china made tourniquet, also will compare it with CAT ones.
As for now we can say that  stretching happens at initial loading, but not happen after all set.
Presumably this discussion can lead to recommendations for picking materials.
I was able to turn china made tourniquet for 720  degrees max, while for home made to get same force load i had to turn it for 1260. 
As for next step to test, I will gather straps with smaller "step", same as on china example. Seems like as smaller step of strap, as tighter it is - means should give less stretch.
For the slicing/printing details I will create separate issue, have some notes also.

![image](https://user-images.githubusercontent.com/12294794/170871097-46c0320d-00b4-436d-815d-fcc691f5a6c5.png)

**Comment by apopanda** [comment]
The windlass isn't a helicopter. More turns doesn't mean better. The tourniquet is supposed to stop bloodflow after ~3, maybe 4 half turns, but have a significant overhead so it doesn't break. It expanding on initial load means the material isn't suitable. Try a heavy nylon webbing, it should stay put, even with multiple uses. Also that thing you're wrapping them on doesn't seem suitable for checking tourniquets, the backing plate should bend over the leg for instance, while on your photo it's rigid straight.

**Comment by alexgubanow** [comment]
Exactly, too many turns suggest that material stretched, a lot.
We just got few samples of 25mm straps, will report about results later.
The same red tube used to test the original tourniquet, while it was possible to turn only for 720 degrees. Based on that, my assumption is whatever sample will be tested, should not go above 720 degrees.
I’m looking for some piece of wood or something, to remove questions here.

**Comment by apopanda** [comment]
Well, a piece of wood / hard stuff isn't ideal either. Don't base your tests on the chineese ones, only original CAT should be the norm, and even those fail 20% of the time according to some data we've found. 
The ukrainian test centers test their tourniquet on live patients, and check for pulse with doppler USG. They do a bunch of other stuff too, but @tareko has mentioned that their testing seems counterproductive (i.e. why do you need a walk test for someone who needs a tourniquet on their leg). For destructive testing we're still looking for solutions. The 720 degree as a baseline isn't a good one though, I personally had one that went up to 8 half rotations (when people use "turns" in regard to tourniquets here, they usually mean one hand movement, so 180 degrees). You needed to use a metal rod for it, and it lost all plastic, but you could turn it that way. I think I saw 6 halfturns as the recommended maximum?

The issue here is that we don't have a reliable testing framework for them yet. Number of turns isn't one that we should compare, since it's too dependant on other factors. You can't turn too much, or you heighten the risk of amputation and other bad stuff happening. You can't have a tourniquet that works up to 4 halfturns, or you risk an unexperienced user breaking them when they need them most, when they give them a "one more for good measure".

**Comment by alexgubanow** [comment]
let me make my point clear, this issue is aimed to find best suite material, only.
Testing of final product will be conducted, after we find suitable materials. 
The test was carried at home with whatever tools was available. Today we hope to measure collected strap samples with tensile machine. We will compare properties of materials used in CAT against what available to us here.

About framework for final product testing, We will send 5-10pcs to Kharkiv medics to test, not to the army guys. The approach with ultrasonic is good one, will see what else option we have.
At the very moment, paramedics simply washing used tourniquets and use it again. we simply can't standstill.

**Comment by apopanda** [comment]
@tareko will be going back through Cracow in the beginning of June and he'll meet with me. He'll be grabbing some materials and taking them to Canada, so Glia can check them out and give their stamp of approval. Glia doesn't have a lab for testing those though, so it'd be mostly comparing to what they use in Canada to make the original ones. You can contact me at adam.popanda@gmail.com, send me the link to ones you'd like to test which I can get in Poland. I'll get them and throw them in for Tarek's goodie bag. The sooner I'd get that, the better, since I don't exactly know when Tarek will be going through here and whether a courier could get here in time. Mostly talking about inner straps. 

RE: "we simply can't standstill" - we can, and we have to. We can't rush into tourniquet production. There's already too many projects that do that and send tourniquets that break. There's huge stigma surrounding 3dp tourniquets in Ukraine currently because of "innovative" projects. I think Tarek has a blogpost about this specific issue. Glia's design is tested in Gaza, but it still has room for improvement. We've seen people replicate the design and make huge mistakes. Even Glia made mistakes in some of the units sent to Ukraine. 

I love your enthusiasm. It's great that there are people out there doing stuff, making tourniquets. The issue is that it's a complex piece of medical equipment which kills people when it fails. We need to be 110% sure it won't fail before sending them out for testing. Otherwise they'll reject every single one, including ones that'd work after the mistakes are fixed.

**Comment by tareko** [comment]
Hey guys! Well done on getting this far, @alexgubanow ! And thank you so much @apopanda for your great comments. I echo many of @apopanda's observations about the importance of careful testing, and I feel like @alexgubanow you and your team are working hard on this.

In terms of the material, from the photos it does seem that the weave is too 'loose'. We are also trying to generate an appropriate specification for the internal belt, so I share with you the sentiment that it is not well-enough characterized in our documents and indeed in the industry.

One simple rule is that the internal strap should consist of material made for rock climbing like [this one](https://www.mec.ca/en/product/5020-829/1%22%2825mm%29-Nylon-Tubular-Climbing-Webbing) (I haven't looked, so don't take this as an unqualified endorsement). That seems to be the one distinction between the high-quality and low-quality straps we've found.

We're working now on a proper specification, but this has proved difficult as manufacturers don't often report it that way. However, stick with the rule of 'climbing strap', and you should be OK.

**Comment by alexgubanow** [comment]
Yeap, we can see same relation in our tension tests today with tensile machine.
Just so you all know my background, I'm 3rd year PhD student of VGTU, Biomechanics. My topic is numerical models of heart mitral valve. But I do many "mechanics" as well. Never the less, the professor from "properties of materials" pointed for - we better do twisting and load over time tests, as it will cover all stress tourniquet is experiencing.
The length for stretch test is about the same is in action on leg and is ~60cm.
I will draw some nice charts from data in matlab later, very busy packing parcel to Ukraine for tomorrow.
The best from today - gave about 240kg load while 70mm stretch.
![photo_2022-05-31_00-47-58](https://user-images.githubusercontent.com/12294794/171062171-2c5f59d4-704a-4695-8b5d-eec02af1f4cc.jpg)
![photo_2022-05-31_00-47-57](https://user-images.githubusercontent.com/12294794/171062175-10bbd3e5-df7f-42ca-9fba-d53f9478b22a.jpg)

short video of setup
https://user-images.githubusercontent.com/12294794/171061627-c07d9563-6df1-4b04-a444-7f6cfc303957.MOV

**Comment by jenwilsonglia** [comment]
@alexgubanow Wondering if you have the data from your tests. We've conducted tensile strength tests on our inner strap webbing materials. You can find these at https://github.com/GliaX/tourniquet/blob/master/assembly_instructions/quality_control/inner%20belt%20tensile%20strength%20notes.md

**Comment by alexgubanow** [comment]
hi, i have not saved the tests. from what i recall, the most suitable material was a safety belt from car.

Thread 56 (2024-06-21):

### ISSUE TITLE
[FEATURE REQUEST] Add release

### ISSUE THREAD

**Issue by darigovresearch** [GliaX/tourniquet#56]
Would be nice to have a V1.0.0 (or a V0.1.0) release in GitHub to make it clearer to see when there are major & minor releases.

Instructions on how to do this for reference can be seen [here](https://docs.github.com/en/repositories/releasing-projects-on-github/managing-releases-in-a-repository)

**Comment by jenwilsonglia** [comment]
We'll put this on the agenda for the next tourniquet meeting on Oct. 18th

**Comment by jenwilsonglia** [comment]
This will be discussed with Tarek for final decision as to the version numbering.

**Comment by jenwilsonglia** [comment]
Current version of parts will be on the repo, but we won't be changing the version names. The most up-to-date parts should be used as the most current version. Once the parts have been updated, the previous version should no longer be used.

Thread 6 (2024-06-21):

### ISSUE TITLE
Translate assembly instructions to Russian

### ISSUE THREAD

**Issue by tareko** [GliaX/tourniquet#6]
David O agreed to do this.

**Comment by tareko** [comment]
We can work here, @denysgochar. As per your offer in Issue #16. Thank you!

**Comment by DenysGonchar** [comment]
Working on it, will submit translation today/tomorrow.

**Comment by defo89** [comment]
Do you need help with this translation?

**Comment by DenysGonchar** [comment]
The translation is done, but after a proof reading a couple of points are identified as unclear. Currently I'm working on additional graphic materials, to avoid any misinterpretation. Would you like to review it once it's done?

**Comment by defo89** [comment]
Sure, if Russian skills is the only pre-requisite, I am happy to review your PR.

**Comment by darigovresearch** [comment]
Is this issue okay to close as there are currently assembly instructions in Russian?

https://github.com/GliaX/tourniquet/blob/master/assembly_instructions/INSTRUCTIONS_RU.md

**Comment by DenysGonchar** [comment]
I think so.

**Comment by jenwilsonglia** [comment]
Closing due to Russian assembly instructions having been translated.

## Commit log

2017-02-27 first design for printable tourniquet parts
    [touniquit.scad, tuniquit_rod.stl, tuniquit_strap.stl]
2017-02-27 Renamed files
    [rod.stl, strap.stl, tourniquet.scad]
2017-02-27 Split file into variables and working files Add more comments
    [rod.scad, strap_holder.scad, tourniquet.scad, variables.scad]
2017-02-28 adding mor details explaining the codes
    [rod.scad, strap_holder.scad, variables.scad]
2017-03-05 Remove unneeded plate and reduce latch size to accept all notches
    [strap.stl, strap_holder.scad, variables.scad]
2017-03-06 adding design for buckle
    [buckle.scad, buckle.stl]
2017-03-06 increasing the clearance between the windlass latches
    [buckle.scad, variables.scad]
2017-03-07 buckle SCAD code explained
    [buckle.scad]
2017-03-18 wider windlass holder and less space for the rod to play in the windlass
    [variables.scad]
2017-03-22 adding two different locking mechanizem for buckles
    [lock buckle.scad, mechnianical buckle.scad]
2017-04-02 adding enhanced version of the buckle
    [lock_buckle_v2.scad, lock_buckle_v2.stl]
2017-04-04 thicker rear bar on buckle lock
    [lock_buckle_v2.scad, lock_buckle_v2.stl]
2017-05-25 Rename buckles
    [buckle.scad, buckle.stl]
2018-04-10 Final tourniquet design
    That the same design like the CAT
    [anchor-Buckle.scad, anchor-Buckle.stl, anchor-holder.scad, anchor-holder.stl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]
2018-04-10 Revert "Final tourniquet design"
    This reverts commit d27f4665d46426454f868b883f9f23e66304626e.
    [anchor-Buckle.scad, anchor-Buckle.stl, anchor-holder.scad, anchor-holder.stl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]
2018-04-10 Final Cat tourniquet
    [anchor-Buckle.scad, anchor-Buckle.stl, anchor-holder.scad, anchor-holder.stl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]
2018-05-12 Rename files over old versions
    [anchor-Buckle.scad, anchor-Buckle.stl, anchor-holder.scad, anchor-holder.stl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]
2018-12-06 insert the comment
    Description the code line of all files by
    [Slice.scad, Slice.stl, anchor-holder.scad, anchor-holder.stl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]
2018-12-06 Revert "insert the comment"
    This reverts commit 8fb5ecd905ac5f9de2e4e70f360902b20599ada4.
    [Slice.scad, Slice.stl, anchor-holder.scad, anchor-holder.stl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]
2018-12-06 Insert the comment
    Description the code line of all files by insert the comment
    [Slice.scad, Slice.stl, anchor-holder.scad, anchor-holder.stl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]
2019-12-08 edit the support slice
    [Slice.scad, Slice.stl]
2019-12-17 Rename and rearrangement the files, make a clip curves more smooth, delete the old file and version number from buckle.
    [Clip.scad, Clip.stl, Rod.scad, Slice.scad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]
2019-12-20 Rename files to be lower case and clearer names
    [backing_support.scad, backing_support.stl, clip.scad, clip.stl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]
2022-03-03 Move STLs and make only 3MF available with correct settings.
    [backing_support.scad, backing_support.stl, buckle.scad, buckle.stl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]
2022-03-05 Clarify documentation and add some measurements (#11)
    * Add more details and dimensions to written instruction.
    * Remove double space after period.
    * Revert size changes for now until examined by Gaza team; give generic and trade name for hook and loop (velcro)
    * Revert incorrectly changed 15->20cm length
2022-03-07 Move to assembly instruction folder
2022-03-08 Correct strap and velcro width. 4cm was too wide.
2022-03-09 Add injection molding files
    [backing_support.stl, buckle_back.stl, buckle_front.stl, clip_moving_part.stl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]
2022-04-14 Clarify English instructions (#23) per @jo-majs
    * Add thickness of strap
    * Added glue for PETG
    * Add zigzag stitch suggestion to point 2
    * Update point 10 and 11
    10: Add slack on internal belt. 11: Specify the 3 cm distance should be between bridge and stitching.
    * Add troubleshooting suggestion: masking tape
    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
2022-04-20 Remove Glia branding
    [buckle.scad, buckle.stl, tourniquet.3mf]
2022-04-25 adding illustrations for assembly instructions
2022-04-25 adding illustrations to the Ukrainian assembly instructions
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2023-02-01 Desktop injection molds prototypes, readme warning. Clip not functional due to model error.
    [backing_plate_injection_mold_tolerances.FCStd, buckle_injection_mold_tolerances.FCStd, clip_injection_mold_tolerances.FCStd, windlass_injection_mold_tolerances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]
2023-02-01 Added the nozzle aluminium seat with initial facing / roughing operations
    [nozzle_slot.FCStd]
2023-02-12 Increased the buckle runner to 4mm, mirrored on both sides. Increased nozzle slot to 4mm to match. Buckle now confirmed to be working with our setup.
    [buckle_injection_mold_tolerances.FCStd, nozzle_slot.FCStd]
2023-02-16 Changed runners in desktop mold.
    [backing_plate_injection_mold_tolerances.FCStd, clip_injection_mold_tolerances.FCStd, windlass_injection_mold_tolerances.FCStd]
2023-02-17 Add quality inspection documentation (#31)
    * Adding quality control documentation
    * Line 70 - should be measured from the bridge on the backing plate, rather than from the face.
    * Lines 40 and 41 - Does the backing plate have damage around the hole on the left side? Has the rivet stressed the plastic plate? There should be a note in the instruction regarding the insertion of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
    ---------
2023-03-05 modified clip mold to reduce shattering
    [clip_injection_mold_tolerances.FCStd]
2023-03-05 added the initial version of the milled / aluminum mold. CAD only.
    [windlass_injection_mold_milling.FCStd]
2023-03-13 Add FreeCAD model files for injection mold (#38)
    [Assembly.FCStd, backing_support.FCStd, buckle.FCStd, clip.FCStd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]
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2023-03-14 Revert "Clarifying 3D printing parameters."
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2023-03-30 Added Denys' Illustrations to Updated EN Instructions and changed Korin's photo 60A1 (#43)
    * Update INSTRUCTIONS_EN.md
    * Update INSTRUCTIONS_EN.md
    * Add files via upload
    * Add files via upload
    * Added Denys' illustrations to EN instructions.
    * Add modified photo to quality_images to show correct dimension.
    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
2023-04-05 redesigned the clip mold - changed the parting line, added a secondary runner
    [clip_injection_mold_tolerances.FCStd]
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2023-04-07 added the buckle for milling
    [buckle_injection_mold_milling.FCStd]
2023-04-07 adding the milled backing plate mold CAD
    [backing_plate_injection_mold_milling.FCStd]
2023-04-07 removed glia.org branding from the buckle
    [buckle_injection_mold_milling.FCStd, buckle_injection_mold_tolerances.FCStd]
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2023-04-15 fixing misaligned windlass in alu mold
    [windlass_injection_mold_milling.FCStd]
2023-04-30 added vent relief to the clip injection mold. Widened the windlass alu injection mold land lengths to prevent bowing out.
    [windlass_injection_mold_milling.FCStd]
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2023-05-22 added vent relief to buckle alu mold
    [buckle_injection_mold_milling.FCStd]
2023-06-30 Added the v1 of the inner strap spacer.
    [spacer.FCStd, spacer.stl]
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2023-07-19 adding vent relief to backing plate mold
    [backing_plate_injection_mold_milling.FCStd]
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2023-08-23 Added BOM files
    [bill_of_materials_glia_poland.ods]
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2024-04-02 Correcting description of Adhesive and Non-Adhesive hook and loop
    Correcting description of Adhesive and Non-Adhesive hook and loop in Material Quantity and Length table. Non-Adhesive hook must be white so that writing can be visible. Adhesive hook can be any colou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
2024-05-29 Adding backplate tester for use testing backplates after printing.
    [TQ backplate tester.STL]
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2024-06-27 Uploading updated tourniquet 3mf file for printing
    3mf file of updated tourniquet parts - all 4 parts on bed (no logo)
    [tourniquet.3mf]
2024-06-27 Updating stl part files
    stl files of each updated part uploaded (buckle without logo)
    [backing_support.stl, buckle.stl, clip.stl, windlass.stl]
2024-06-27 Uploading updated FCStd part files
    Adding updated FreeCAD files for each part to CAD folder (buckle without logo)
    [backing_support.FCStd, buckle.FCStd, clip.FCStd, windlass.FCStd]
2024-06-28 Delete source_files/CAD/windlass.scad
    updated windlass is uploaded to CAD folder as a FreeCAD file
    [windlass.scad]
2024-06-28 Delete source_files/CAD/clip.scad
    Updated clip was uploaded to CAD folder as a FreeCAD file.
    [clip.scad]
2024-06-28 Delete source_files/CAD/buckle.scad
    Updated buckle was uploaded to CAD folder as a FreeCAD file.
    [buckle.scad]
2024-06-28 Delete source_files/CAD/backing_support.scad
    Updated backing_support was uploaded to CAD folder as a FreeCAD file.
    [backing_support.scad]
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2025-07-11 Reorganization of QC folder, documents and information. (#74)
    * Moving QC folder out of assembly instructions, and incorporating strap spacer into QC folder
    * Create Readme.md for QC folder
    This contains all information on Quality Control files for this device.
    * Update Readme.md for Quality Control
    Modifying strap spacer information
    * Update Readme.md for
    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
    [TQ_backplate_tester.STL, strap_spacer.FCStd, strap_spacer.stl]
2025-07-11 updating broken links to strap spacer and QC folder in Step 10
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
